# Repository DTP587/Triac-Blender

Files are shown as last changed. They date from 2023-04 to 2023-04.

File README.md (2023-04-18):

# Triac Blender
_Blender with Triac v1, Build Notes. Part of the Open Science Framework repository [OpenLPE](https://osf.io/evupy/)_

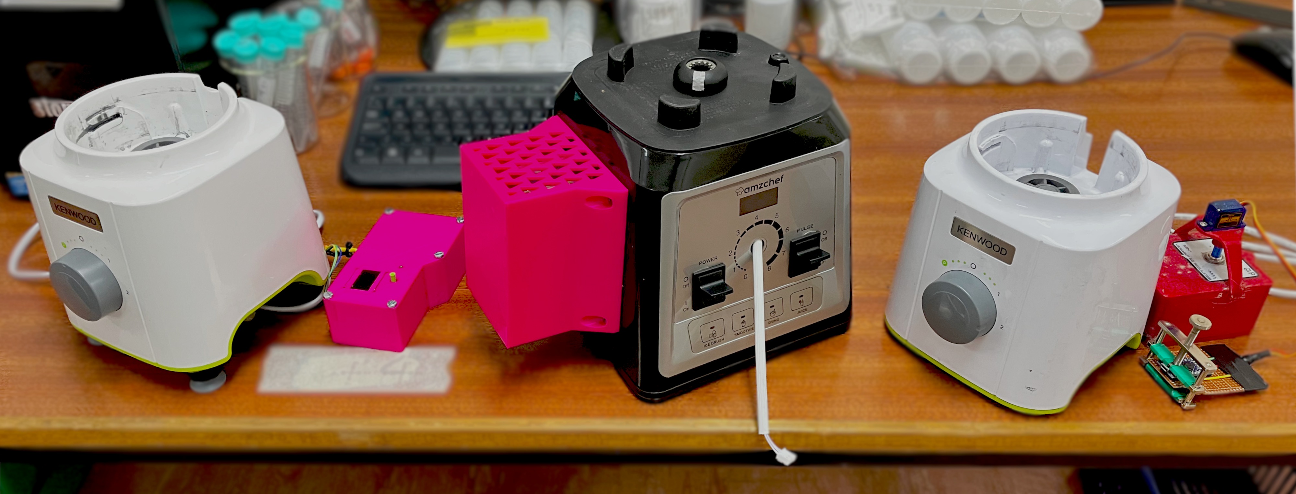
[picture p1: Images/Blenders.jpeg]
Image of all three blenders in order


_From right to left, Triac-Blender v1, Triac-Blender v2, PID-Blender._

### Background \& Motivation

_This is part of the [OpenLPE](https://osf.io/evupy/) labware project._

There are no reasonably priced commercial blenders with adequate speed control for practical experiments. The closest is the [Waring LB20ES](https://www.thelabstore.co.uk/waring-lb20es-variable-speed-control-blender-1-0-litre-stainless-steel-container-230v-50-hz-ce-approved-rohs-with-european-f-schuko-plug.html), being over £1000. This left us feeling priced out, so we had to come up with an alternative, which is this Triac modification, enabling for great power selectivity. Speed is unreliable at low speeds (< $2000$ $rpm$), but stays pretty constant at higher speeds ($\pm\;1000\;rpm$).

The blenders I have been controlling range between $600$ $W$ to $2$ $kW$ peak power, which they can sustain for a maximum of $\approx 1$ $min$ before they get dangerously hot (and melt-y). Some come with automatic sensors to detect when they are overheating and shut-off automatically to save the motor. From my testing, I recommend following the manufacturer's recommendations alternating running it for $1$ $min$ **ON** with a subsequent minimum of $1$ $min$ **OFF** to allow it to cool down.

### Disclaimer!

Playing with AC is _incredibly_ dangerous. Make sure to take all precautions when making modifications and ensure everything is unplugged and grounded.

## Potential Changes

List of changes and whether they have been implemented.

- [ ] The box is not the perfect size, needs to be a little wider to fit the dimmer, probably would be nice to add a different 
- [ ] Could end up making our own circuit [for arduino](https://circuitdigest.com/microcontroller-projects/ac-phase-angle-control-for-light-dimmers-and-motor-speed-control-using-555-timer-and-pwm-control) as there are some well documented [methods](http://www.simulation-research.com/help/userguide/drives_phaseanglecontrol.html).

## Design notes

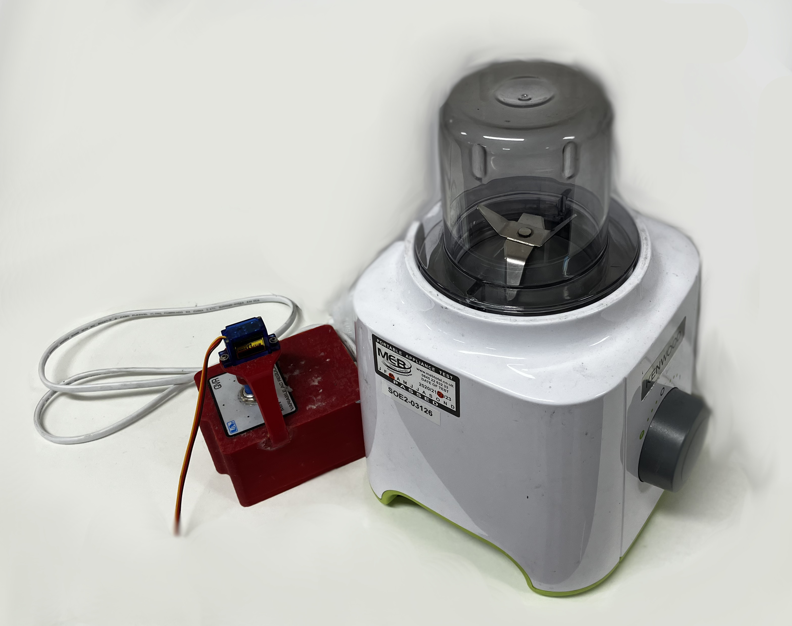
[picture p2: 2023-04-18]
Images/Dimmer-v1.jpeg

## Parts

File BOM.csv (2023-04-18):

Item | Link | Qty | Price per Unit | Cost | Description
Kenwood BLP31.D0WG | https://www.argos.co.uk/product/8132303 | 1 | £53.00 | £53.00 | Decent blender with good power output at a nice price point.
United Automation QVR-TB-RFI | https://uk.rs-online.com/web/p/thyristors/2143963 | 1 | £64.30 | £64.30 | Overkill SCR circuit with potentiometer control.
Heat Shrink |  | - | - | - | To protect soldered collections.
Soldering iron |  | - | - | - | Solder wires together.
Red wire 20 awg ~ 300 mm | https://www.amazon.co.uk/Electrical-Wire-AWG-Extension-Brightfour/dp/B07CGKCJFV | - | - | - | Live wiring, of good gauge to handle the current.
Black wire 20 awg ~ 300 mm | https://www.amazon.co.uk/Electrical-Wire-AWG-Extension-Brightfour/dp/B07CGKCJFV | - | - | - | Neutral wiring, of good gauge to handle the current.
CAD/Upper.step |  | - | - | - | To isolate the live AC and be a little safer.
CAD/Lid.step |  | - | - | - | To isolate the live AC and be a little safer.
M4 countersink 15 mm | https://uk.rs-online.com/web/p/socket-screws/0171837 | 4 | £0.20 | £0.80 | To bolt the potentiometer box lid shut.
 |  |  |  | £118.10

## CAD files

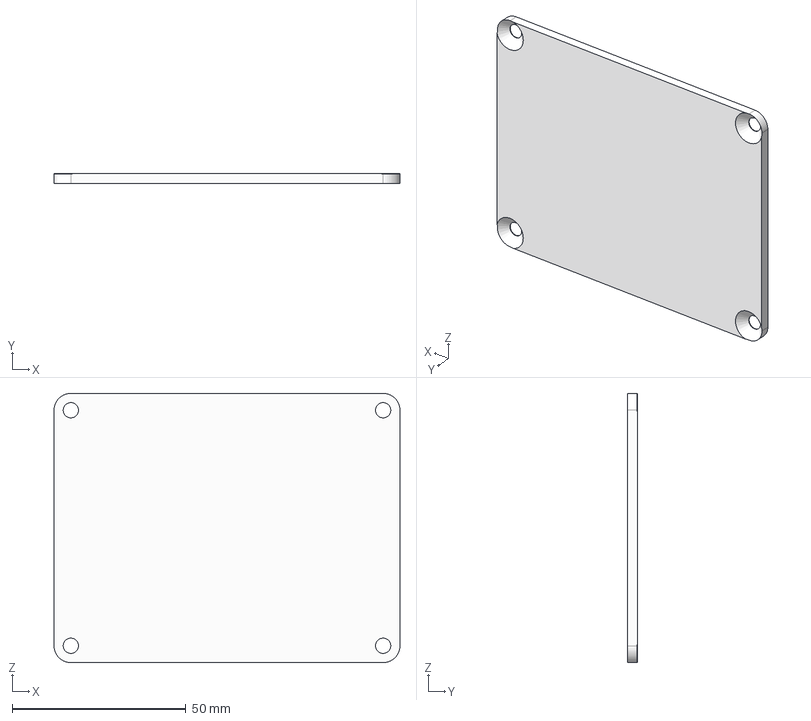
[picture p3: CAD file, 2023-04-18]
CAD/Lid.step
99.6 x 3.00 x 77.5 mm

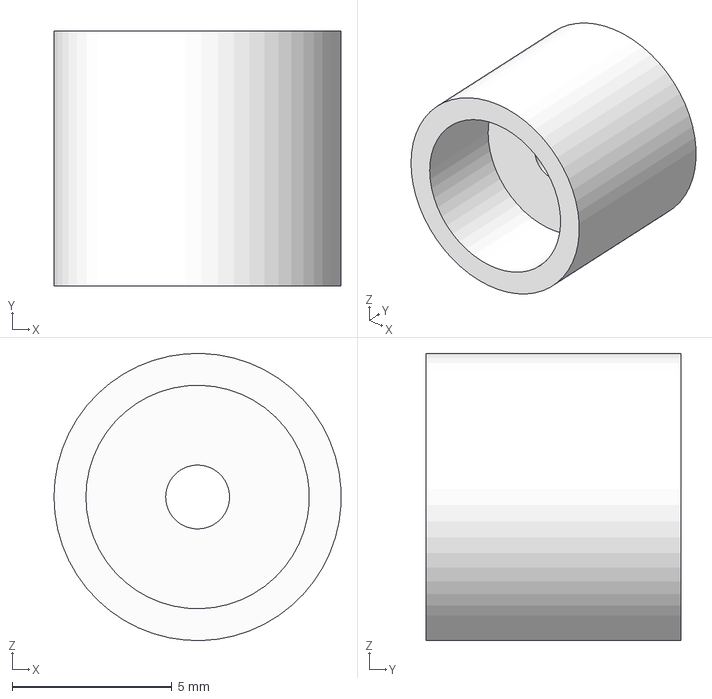
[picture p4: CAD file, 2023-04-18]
CAD/Coupling.step
8.99 x 8.00 x 9.00 mm

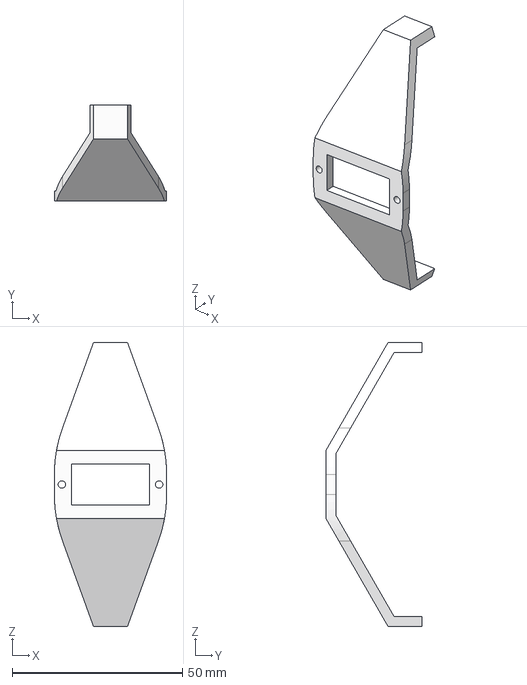
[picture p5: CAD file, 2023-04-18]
CAD/Servo Mount.step
33.0 x 28.3 x 83.5 mm

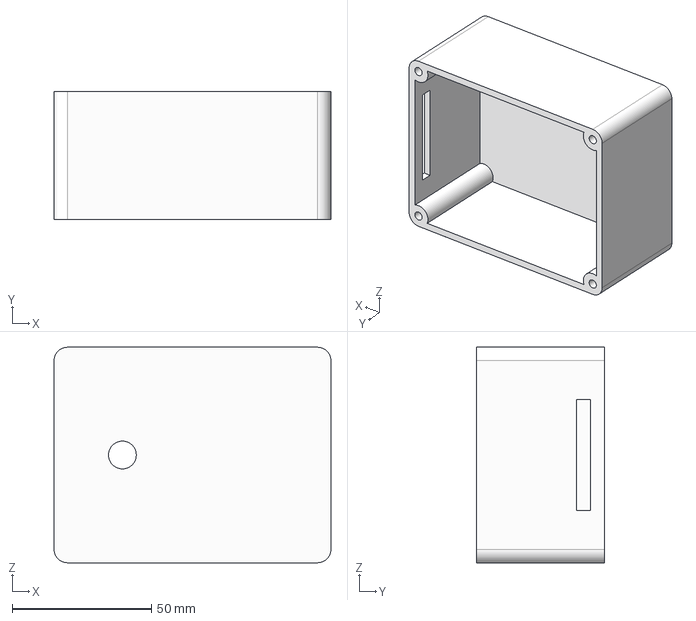
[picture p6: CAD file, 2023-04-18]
CAD/Upper.step
99.6 x 46.0 x 77.5 mm

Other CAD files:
CAD/Dimmer-Box.f3d

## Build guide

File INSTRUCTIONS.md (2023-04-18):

# Build Instructions and Notes

### Operating Principles

This project involves the [phase-angle control](https://electricalacademia.com/electronics/scr-thyristor-phase-control-circuit/) of AC signals. this allows for accurate power delivery but it is important to remember that rotational speed of the blender $\neq$ power.

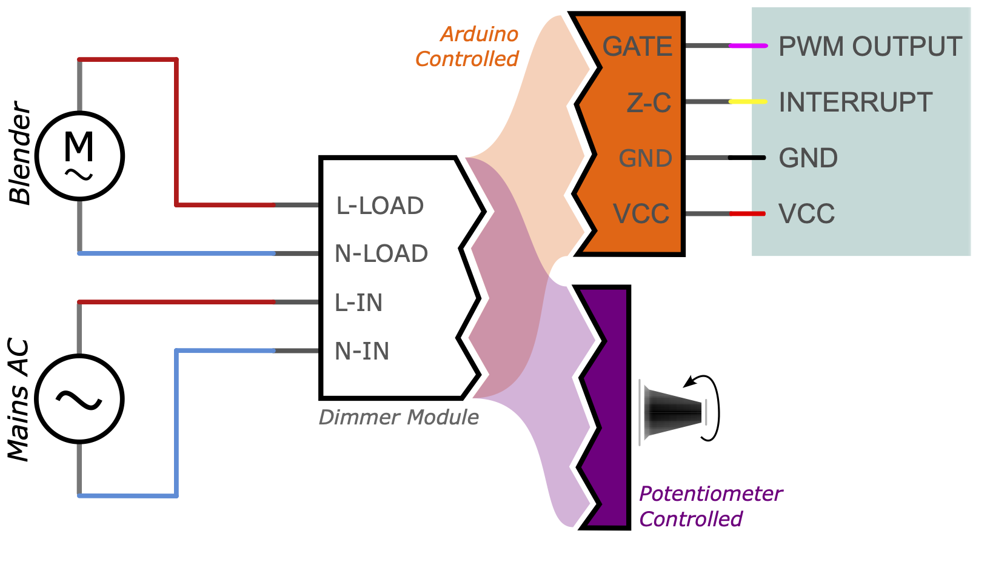
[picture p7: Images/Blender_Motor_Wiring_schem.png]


_Very basic wiring of a dimmer module with potentiometer control or arduino control, depending on the circuit._

Note also, that I found it possible to measure the speed simply from the noise given off by the blender with the [spectroid app for android](https://play.google.com/store/apps/details?id=org.intoorbit.spectrum). Will take some work to recognise which signals are which, but if you are uninterested in exact speed, you can make the setup more repeatable by aiming for previously obtained resonant frequencies!

##### Phase Angle Control

Phase angle control, is a method of controlling the duty cycle of an AC signal every half cycle. This typically uses a triode called a triac sometimes also called a Silicon Controlled Rectifier (SCR) or a Thyristor, and you will often see these terms banded around when shopping circuitry. The circuit is similar to what you would find in a dimmer switch in a house, hence sometimes it is called a dimmer or dimming circuit.

The main advantages to this type of rectification compared to other similar functioning circuits is that:

1. It does not disapate very much energy.
2. Simple to implement.
3. Duty cycle is small for mains AC (100% $\sim 10\;ms$), so the power delivery is pretty constant (no flickering).



_Simple representation of phase angle control._

The AC signal in potentiometer controlled cases is routed through a voltage divider which feeds into the GATE pin of the Triac. The exact electronics and some of the issues surrounding these circuits is well discussed in [this article](https://eepower.com/technical-articles/alternating-current-ac-load-control-with-triacs/#). In arduino controlled units, there will be some sort of isolation between the low and high voltage side, primarily through the use of an optocoupler or [similar circuitry](https://www.circuitar.com/nanoshields/modules/triac/).

## Bill of Materials

[](If you are going to submit a BOM with your build, convert it to markdown and paste it here, as well as including it in the main folder!)

|Item                        |Link                                                                           |Qty|Price per Unit|Cost    |Description                                                 |
|----------------------------|-------------------------------------------------------------------------------|---|--------------|--------|------------------------------------------------------------|
|Kenwood BLP31.D0WG          |https://www.argos.co.uk/product/8132303                                        |1  |£53.00        |£53.00  |Decent blender with good power output at a nice price point.|
|United Automation QVR-TB-RFI|https://uk.rs-online.com/web/p/thyristors/2143963                              |1  |£64.30        |£64.30  |Overkill SCR circuit with potentiometer control.            |
|Heat Shrink                 |                                                                               |-  |-             |-       |To protect soldered collections.                            |
|Soldering iron              |                                                                               |-  |-             |-       |Solder wires together.                                      |
|Red wire 20 awg ~ 300 mm    |https://www.amazon.co.uk/Electrical-Wire-AWG-Extension-Brightfour/dp/B07CGKCJFV|-  |-             |-       |Live wiring, of good gauge to handle the current.           |
|Black wire 20 awg ~ 300 mm  |https://www.amazon.co.uk/Electrical-Wire-AWG-Extension-Brightfour/dp/B07CGKCJFV|-  |-             |-       |Neutral wiring, of good gauge to handle the current.        |
|CAD/Upper.step       |                                                                               |-  |-             |-       |To isolate the live AC and be a little safer.               |
|CAD/Lid.step   |                                                                               |-  |-             |-       |To isolate the live AC and be a little safer.               |
|M4 countersink 15 mm        |https://uk.rs-online.com/web/p/socket-screws/0171837                           |4  |£0.20         |£0.80   |To bolt the potentiometer box lid shut.                     |
|                            |                                                                               |   |              |£118.10 |                                                            |

## Mods

There are no direct modifications to the blender itself, apart from wiring in the dimmer module. In my case, I decided to remove the connections to the main switch dial at the front of the blender, as it didn't add any extra security or control to the blender.

Note that there are much cheaper [pot dimmer circuits](https://www.amazon.co.uk/AITRIP-Control-Controller-Adjustable-Regulator/dp/B08L7NF4Q9) available (at £4.50 a pop), but we decided to go with the overkill option to save any potential headaches. With pot blenders, you can't exactly return to the same power setting unless you have some readout to go with it, for example, a frequency, a precise angle or a power reading. There are [modules](https://www.amazon.co.uk/gp/product/B076VKJM42) which have digital readouts for a more precise reading. Again it is important to stress that precise power $\neq$ precise speed reading.

### Wiring

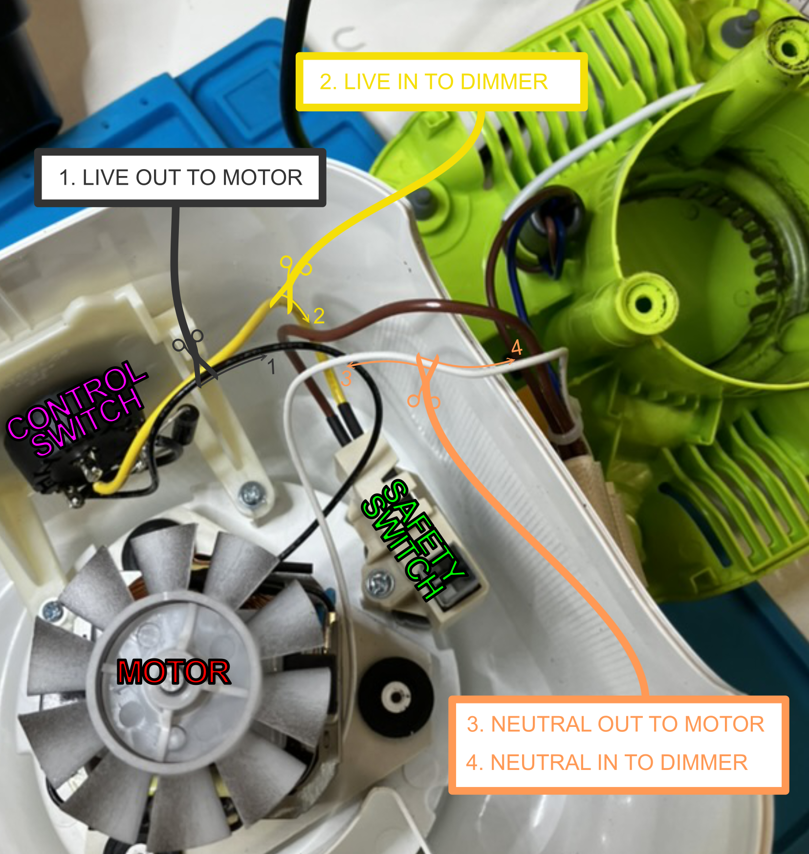
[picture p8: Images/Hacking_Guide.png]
Opened blender with labelled modifications


1.	Unsolder the black wire from the motor to the control switch. This lead is the LIVE AC OUT (**L AC-MOTOR**) to the motor.
2. Unsolder the Yellow Wire from the control switch. This is the LIVE AC IN (**L AC-IN**) to the dimmer.
    
    At this point, the control switch is completely bypassed, but the safety switch isn't. I prefer to keep the safety switch wired in, as it ensures the blender is not live when the jug isnt plugged in.
    
    During my testing, position "P" and "2" on the dial were a simple on off switch (for full AC Power), while position "1" cut the negative half of the waveform.
    
3. The white wire is neutral mains, wired directly to the motor. Cut the wire roughly halfway. This is NEUTRAL AC OUT (**N AC-MOTOR**) to the motor.
4. The other side of the wire cut cut in step 3 is NEUTRAL AC IN (**N AC-IN**) to the Dimmer.

You'll need about half a meter of suitable guage wiring to extend these wires out of the blender. These will take a bit of current, so ensure they are soldered well.

### Printing

CAD files for printing the box are given in the `CAD` folder. There's not much to go into here, as the box offers no extra safety except to hide the wired connection points.

## Arduino Code

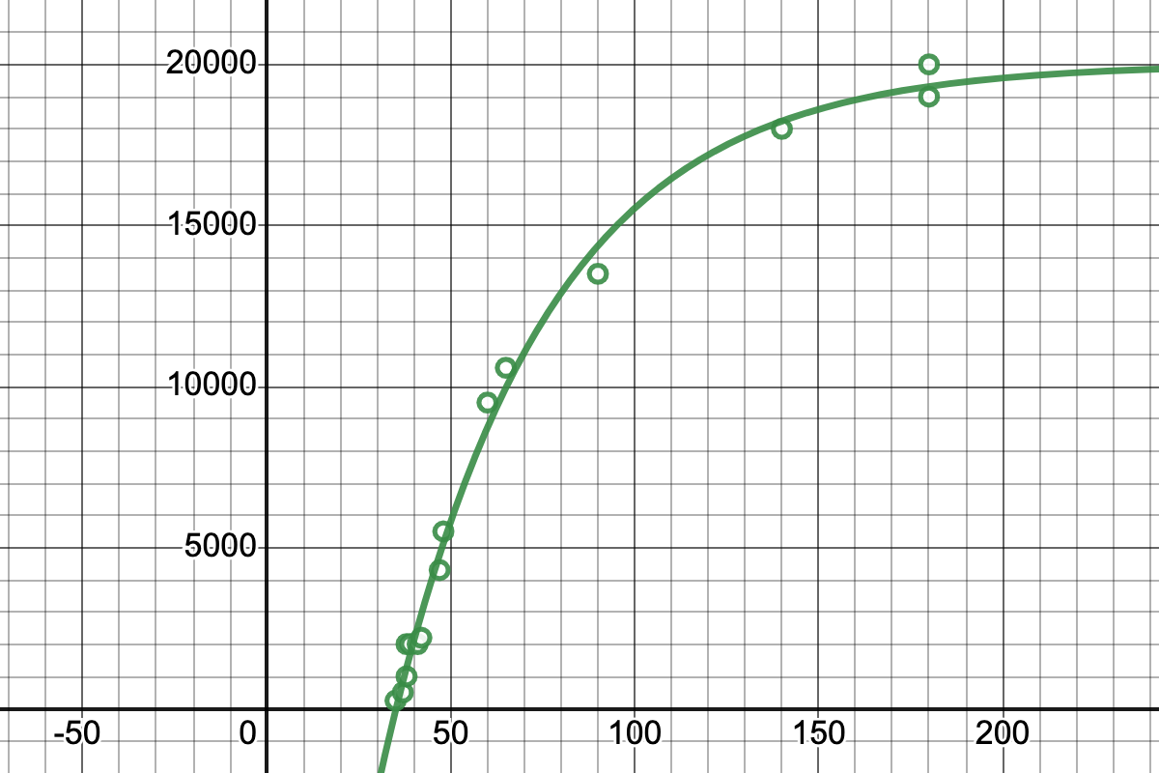
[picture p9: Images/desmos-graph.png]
Blender speed versus servo angle

_Servo angle (x) against rotor speed (y). Notice the sharp dip in speed around_ $\theta$ _= 50 rpm This explains why speed is unreliable here; Small changes at low power settings make the speed very touchy and sensitive to position._

I have since added a small 9g servo to the top of the box to operate the dial (which allows for on-off cycling). As it doesn't affect the main electronics, I'll add the code used to operate it in the code folder. The data is [on desmos](https://www.desmos.com/calculator/bqjuhv8qqg) if you're looking to play around with it.

The addition of the servo is very simple, so I won't get into the details (as there is not much to get into), but consists of adding a mounting arm to the top of the box and a coupling for the servo arm to attatch directly to the potentiometer secured in with a little contact adhesive.

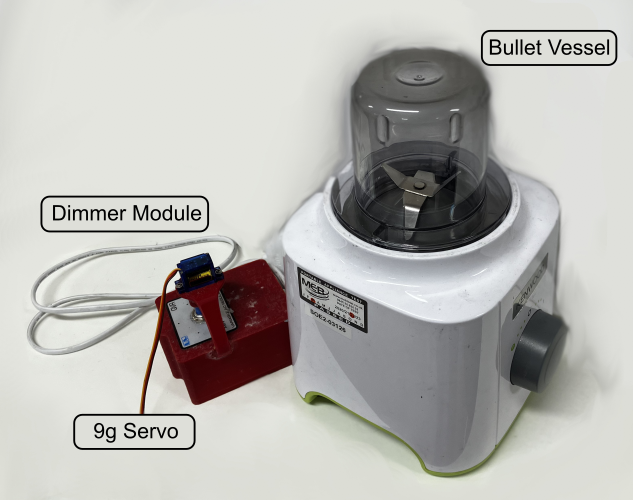
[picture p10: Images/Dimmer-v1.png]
Blender servo arm


_Potentiometer blender with added servo._

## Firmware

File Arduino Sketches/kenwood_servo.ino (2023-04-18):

//---------------------

#include <Servo.h>



Servo servo;



int serv = 3;

float minson = 1.5; //minutes, total time on + off
int offtime = 3; //seconds, off time
int ontime = 15;  //seconds, on time
int angle = 180;  //max 180
                  //90     ~  9'500 rpm
                  //180    ~ 17'000 rpm
int overshoot = 0; // To force the start at low speeds

 

float start;
int gap;
int flip = angle;
bool called = false;





int tic(int t) {

  return round((millis()-t)/1000.);

  }

 

 

int routine(int l) {

 

  start = millis();

  servo.write(flip+overshoot);
  delay(800);
  servo.write(flip);
  
  Serial.println("- - -");
  Serial.print("Tic: ");
  Serial.println("0");

  Serial.print("Angle: ");
  Serial.println(flip);

  Serial.print("Status: ");
  Serial.println("On");

  gap = ontime;
  delay(1010);
 

  while ((float(tic(start))/(60.*l)) < 1) {

    if (tic(start)%gap == 0) {

      Serial.println("- - -");
      Serial.print("Tic: ");
      Serial.print(tic(start));
      Serial.println(" sec");

      if (flip == 0) {

          flip = angle;

        }

      else if (flip == angle) {

          flip = 0;

        }

      servo.write(flip+overshoot);
      delay(800);
      servo.write(flip);

      Serial.print("Angle: ");
      Serial.println(flip);

      if (gap == ontime) {

        Serial.print("Status: ");
        Serial.println("Off");
        
        gap = offtime + ontime;
        
        delay(1010);
        
        }

      else if (gap == offtime + ontime) {

        Serial.print("Status: ");
        Serial.println("On");
        
        gap = ontime;

        delay(1010);
        
        }

      }

    }

  servo.write(0);

  }





void setup() {

  Serial.begin(9600);

  //pinMode(led2, OUTPUT);

  servo.attach(serv);

  }



void loop() {
  
  servo.write(0);
  
  delay(3000);
  Serial.println("_________");
  Serial.println("Connected");
  Serial.print(  "Total ontime: ");
  Serial.println(ceil((minson*60/(ontime + offtime))*ontime/60));
  delay(3000);

  routine(minson);

  Serial.println("- - -");
  Serial.println("Done");

  while (true) {}

  }



//-------------------
